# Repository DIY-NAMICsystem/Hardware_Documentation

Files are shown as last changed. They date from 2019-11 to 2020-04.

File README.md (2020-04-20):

# DIY-Nautiyal Arduino Modular Instrumental Conditioning (DIY-NAMIC) Boxes

<p align="center">
    <br>
    <i> Mouse retrieving water reward during behavioral testing in the DIY-NAMIC system </i>
</p>

<p align="left">
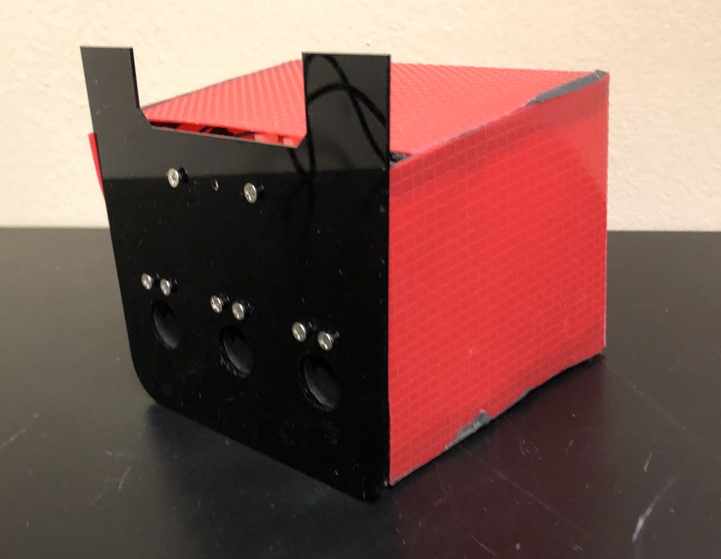
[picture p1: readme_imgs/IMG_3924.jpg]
  <br>
    <b><i> Assembled DIY-NAMIC hardware </b> </i>
    <br>
    <br>
</p>

<p align="left">
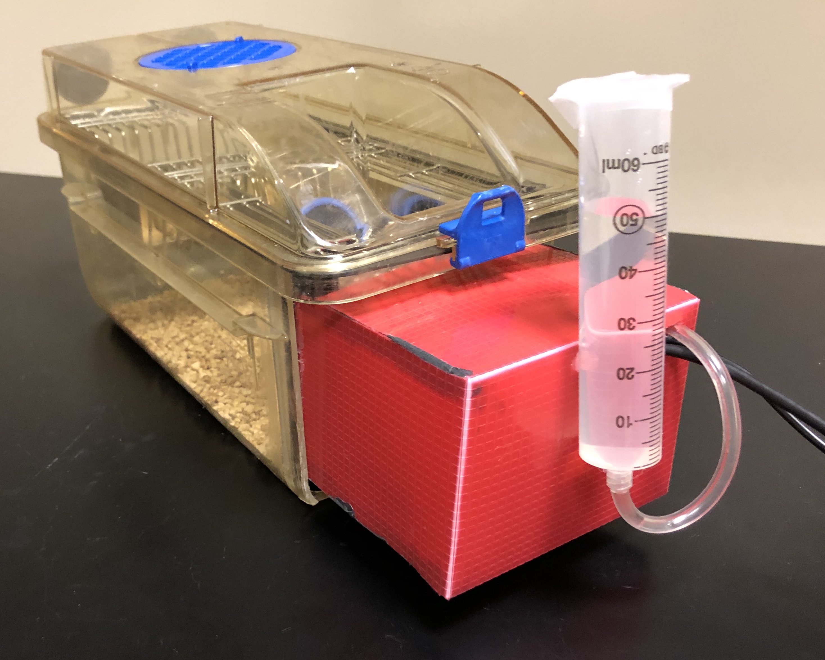
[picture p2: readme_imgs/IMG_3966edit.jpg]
  <br>
    <b><i> DIY-NAMIC cage </b></i>
</p>

<p align="left">
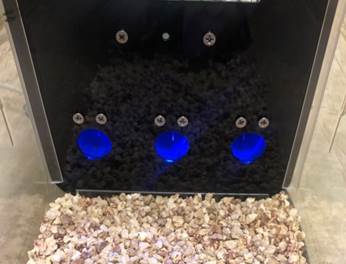
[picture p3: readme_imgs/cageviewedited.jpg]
  <br>
    <b><i> Mouse perspective </b> </i>
    <br>
    <br>
</p>

<p align="left">
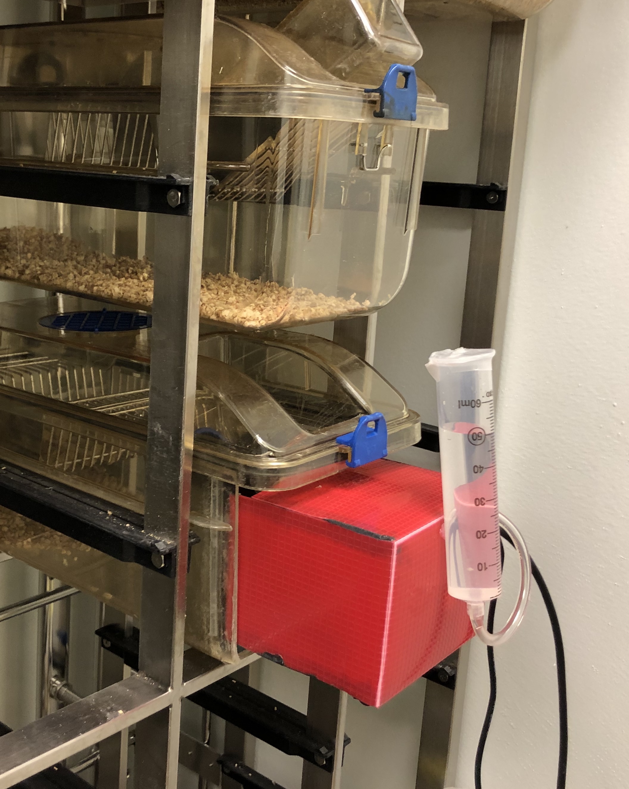
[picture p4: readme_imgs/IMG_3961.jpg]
  <br>
    <b><i> DIY-NAMIC testing is compatible with ventilated high-density racked cages </b> </i>
    <br>
    <br>
</p>

___

### What is DIY-NAMIC?

The DIY-NAMIC box is a customizable, low-cost apparatus for automated homecage operant behavioral testing. Made with Arduino microprocessor, 3D printed parts, and various *off-the-shelf* components, the boxes enable 24-hour data collection, significantly increasing trials/day without food or water restriction, and allowing for self-initiated trials during rodent's dark/active phase.  

Most importantly, this is an open-source project - any contributions / suggestions / feedback are welcome and appreciated!

___
### Benefits of DIY-NAMIC boxes.

1. Decreased Experiment Length <br>
Rodents have 24 hour access self-initiated trials allowing hundreds of trials per day. This allows for faster testing, reducing the number of days that many standard operant paradigms typically takes to run. This also permits testing during developmental time periods which can be very limited in rodents.

2. Inexpensive compared to commercially available operant testing chambers <br>
All the materials used to make one DIY-NAMIC box cost around $200, compared to$4000-$10,000 for the commercially-available units, which have limited customizability.

3. No food or water restriction <br>
Mice consume their normal daily intake of water, and no food deprivation is required.  The sated condition is important for the interpretation of many behavioral effects.  Additionally, this allows testing during development when food/water deprivation can be deleterious to growth.

4. Reduced daily experimenter effort <br>
There is minimal daily effort required from the experimenter, since mice are living in their homecage, and data is logged in realtime.

5. More ethologically-relevant testing <br>
Through self-initiated trials, mice can perform during their standard dark/active phase of the light-dark cycle. 

___
### Overview

The purpose of this repository is to provide **hardware manuals, documentation, and code** for anyone who would like to use and/or modify the DIY-NAMIC system.

#### Contents

* [**Chapter 0 - Background and Introduction**](https://github.com/DIY-NAMICsystem/Hardware_Documentation/tree/master/Chapter_0.Background_and_Introduction) 
* [**Chapter 1 - Getting Started - Essential Tips and Tricks**](https://github.com/DIY-NAMICsystem/Hardware_Documentation/tree/master/Chapter_1.Getting_Started-Essential_Tips_and_Tricks)
* [**Chapter 2 - Modifying the Rodent Cage**](https://github.com/DIY-NAMICsystem/Hardware_Documentation/tree/master/Chapter_2.Modifying_Rodent_Cage)
* [**Chapter 3 - OM1 Shield**](https://github.com/DIY-NAMICsystem/Hardware_Documentation/tree/master/Chapter_3.OM1_Shield)
* [**Chapter 4 - Component Assembly - LED**](https://github.com/DIY-NAMICsystem/Hardware_Documentation/tree/master/Chapter_4.Component_Assembly-LED)
* [**Chapter 5 - Component Assembly - Infrared Detectors**](https://github.com/DIY-NAMICsystem/Hardware_Documentation/tree/master/Chapter_5.Component_Assembly-Infrared_Detectors)
* [**Chapter 6 - Component Assembly - Solenoid Valves**](https://github.com/DIY-NAMICsystem/Hardware_Documentation/tree/master/Chapter_6.Component_Assembly-Solenoid_Valves)
* [**Chapter 7 - Component Assembly - Reward Spout**](https://github.com/DIY-NAMICsystem/Hardware_Documentation/tree/master/Chapter_7.Component_Assembly-Reward_Spout)
* [**Chapter 8 - Wiring and Soldering**](https://github.com/DIY-NAMICsystem/Hardware_Documentation/tree/master/Chapter_8.Wiring_and_Soldering)
* [**Chapter 9 - Final Assembly**](https://github.com/DIY-NAMICsystem/Hardware_Documentation/tree/master/Chapter_9.Final_Assembly)

* [**Appendix - Bill of Materials**](https://github.com/DIY-NAMICsystem/Hardware_Documentation/tree/master/Bill_of_Materials)

____
### Other open-source projects in the behavioral neuroscience community

1. [Feeding Experimentation Device (FED) - Kravitz Lab](https://github.com/KravitzLab/FED)
2. [CombiCage - Loos Lab](https://www.ncbi.nlm.nih.gov/pmc/articles/PMC5309744/)
3. [ArControl - Li Lab](https://github.com/chenxinfeng4/ArControl)
4. [Openmaze.org](http://openmaze.org/) - open source hardware and software for behavioral neuroscience
5. [Openbehavior.com](http://openbehavior.com/) - repository of open source tools for advancing behavioral neuroscience research]

### Development
_____

### Contributions and Thanks
_____

A big thanks to **Andrew R. Alvarenga** for his generous support and suggestions regarding hardware. Thank you for also allowing me to use the machine shop and test out different prototypes of the 3D printed parts on the 3D printer.

Thank you to undergraduate researchers **Bonnie Shea** and **Selin Capan** for assisting with daily running of the code.

#### Contact

For any questions or issues, contact **Jun Ho Lee** at jun.ho.lee@dartmouth.edu or **Katherine Nautiyal** at katherine.nautiyal@dartmouth.edu.

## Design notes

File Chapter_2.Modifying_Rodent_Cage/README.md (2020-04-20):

### Introduction

The DIY-NAMIC system utilizes a rodent homecage for behavioral testing. In this chapter, the standard rodent cage used in ventilated high-density racked systems is modified for use with the DIY-NAMIC system. Using a Dremel to cut a cross-section of the cage, U-channels are attached on the bottom and the sides of the cage, allowing a laser cut plexiglass wall to be slotted in.

### Rodent Cages

This section will require modification based on the available rodent caging systems.

The plexiglass wall must be modified to fit the relevant homecage. They can be modified from our design [(https://github.com/DIY-NAMICsystem/Hardware_Documentation/tree/master/Ponoko_Final)], and cut at Ponoko.com.

> This **location** was chosen due to the design of the cage hopper and the plexiglass. Positioning the U-channel at this location will minimize the gaps between the metal hopper and the plexiglass **(Figure 4 and Figure 5).**

For the purposes of exposing the cross-section, draw a line at the 5cm mark (see yellow arrow) at an angle **(Figure 2)** on both sides of the cage. These lines will always be posterior relative to the bottom U-channel position and thus will serve as good guidelines for cutting the cage later.

<p align="center">
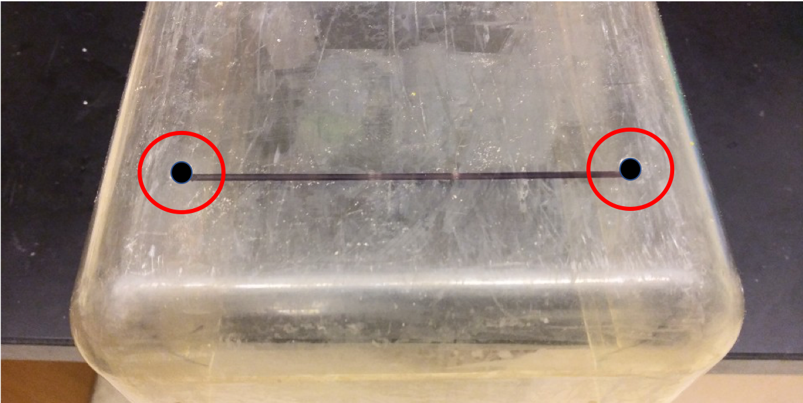
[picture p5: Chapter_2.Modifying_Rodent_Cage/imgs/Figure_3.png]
    <br><br>
    <b><i>Figure 3:</b> The two protruding circles (filled with black circles within red bounded circles) are connected with a black Sharpie marker. This will later serve as the bottom U-channel position. </i>
</p>

<p align="center">
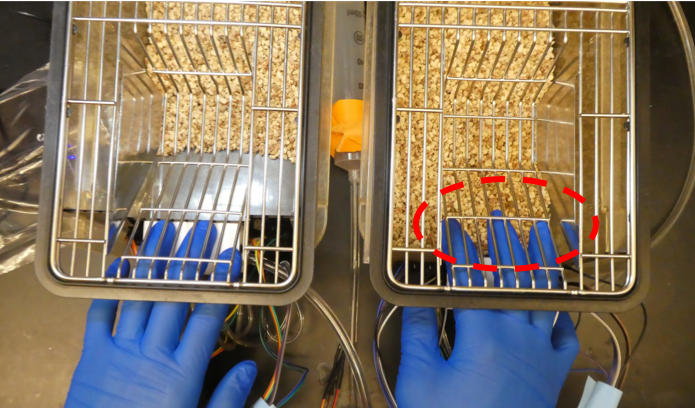
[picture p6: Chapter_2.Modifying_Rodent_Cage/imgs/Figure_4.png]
    <br><br>
    <b><i>Figure 4:</b> Faulty positioning of the U-channel will result in gaps between the plexiglass and the metal hopper (Red Circle) </i>
</p>

<p align="center">
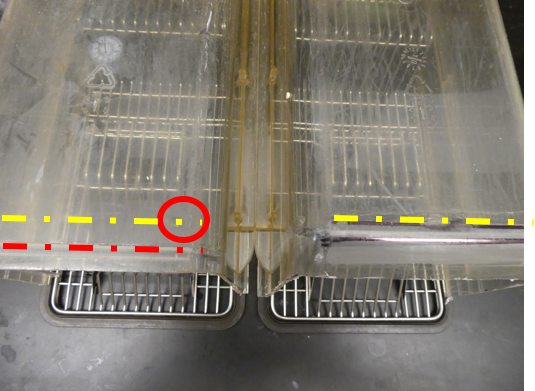
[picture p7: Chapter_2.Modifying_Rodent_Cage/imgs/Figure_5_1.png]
    <br><br>
    <b><i>Figure 5:</b> Yellow dotted lines indicate the correct location for positioning the bottom U-channel. Red dotted lines indicate a faulty position that will create a gap between the metal hopper and the plexiglass. </i>
</p>

### Cutting the Cage

When cutting the cage, make sure to cut the sides first. Remember that the sharpie mark at the bottom is where the U-channels are going to align, **NOT** where it will be cut. Cutting the sides first will prevent you from making that mistake.

<p align="center">
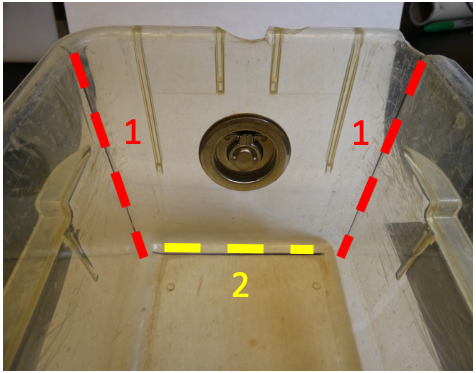
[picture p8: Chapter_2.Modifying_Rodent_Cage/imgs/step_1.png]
step1
    <br><br>
    <b><i>Step 1:</b> Cut the cage according to the numbers shown - Sides (Red) first and then the bottom (Yellow) of the cage. </i>
</p>

<p align="center">
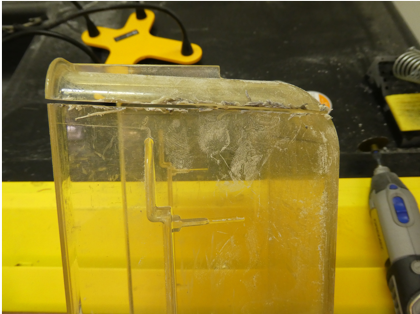
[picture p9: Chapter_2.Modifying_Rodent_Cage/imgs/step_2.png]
step2
    <br><br>
    <b><i>Step 2:</b> Cutting along the sharpie mark along the two sides </i>
</p>

<p align="center">
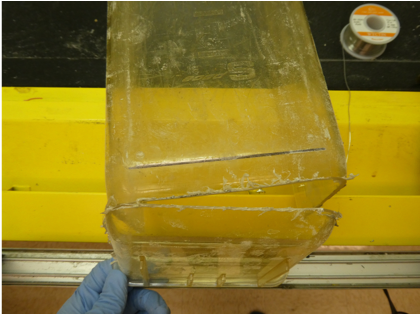
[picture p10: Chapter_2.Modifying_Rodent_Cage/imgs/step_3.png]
step3
    <br><br>
    <b><i>Step 3:</b> All three sides (two sides + one bottom) have been cut and ready to be separated from the main cage body. </i>
</p>

The Dremel rotary tool will produce a lot of fine dust so work in a well-ventilated area. After the initial cut, wash off the fine dust by running the cage under water. After thoroughly drying it, you may also want to use the belt grinder to sand down the sides for a smoother, cleaner finish.

<p align="center">
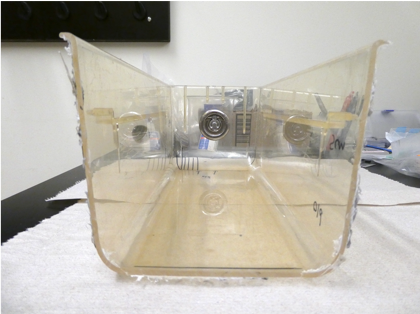
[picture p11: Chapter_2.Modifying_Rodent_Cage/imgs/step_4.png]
step4
    <br><br>
    <b><i>Step 4:</b> Cross Section of the cage right after the Dremel cut. Notice the rugged, sharp edges. </i>
</p>

<p align="center">
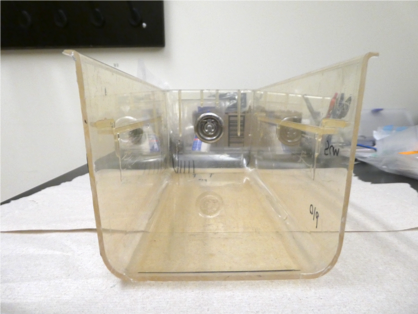
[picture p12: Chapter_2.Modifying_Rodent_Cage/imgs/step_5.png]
step5
    <br><br>
    <b><i>Step 5:</b> Cross section of the cage after sanding it down with the belt grinder. </i>
</p>

### Attaching the U-Channels

<p align="center">
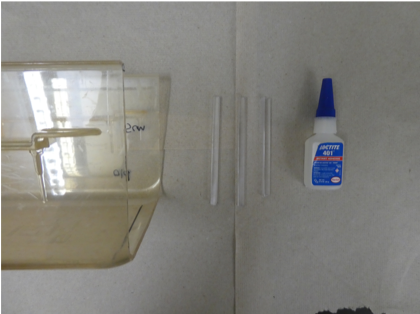
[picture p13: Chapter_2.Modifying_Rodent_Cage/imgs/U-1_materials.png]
materials
    <br><br>
    <b><i>Materials Needed:</b> Loctite Glue (401) / U-channels / Rodent Cage </i>
</p>

<p align="center">
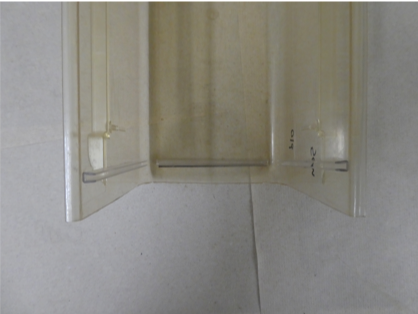
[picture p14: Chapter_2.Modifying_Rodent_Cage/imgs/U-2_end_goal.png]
endgoal
    <br><br>
    <b><i>End Goal:</b> Picture of the completed modified cage after attaching the U-channels </i>
</p>

Two U-channels (11.3cm long) will go on the sides and one U-channel (10.3cm long) will go on the bottom.

The U-channels serve as guides for the plexiglassto be slid in. Therefore, all three should be aligned and flat with the surface of the cage. It is easier to align all three of them together if the bottom is attached first. Then, align the side U-channels by using the bottom U-channel as a reference point.

<p align="center">
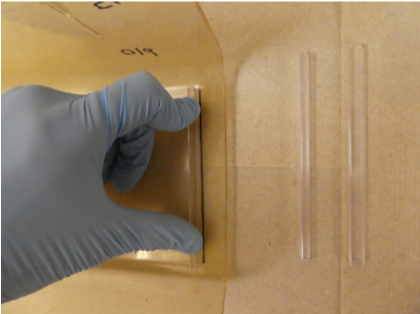
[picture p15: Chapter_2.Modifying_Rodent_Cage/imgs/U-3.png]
u1
    <br><br>
    <b><i>Step 1:</b> Attaching the bottom U-channel first. Apply Loctite glue along the back of the U-channel and align it along the black sharpie mark and hold it down for a few seconds to get a good attachment. Let it cure overnight. </i>
</p>

<p align="center">
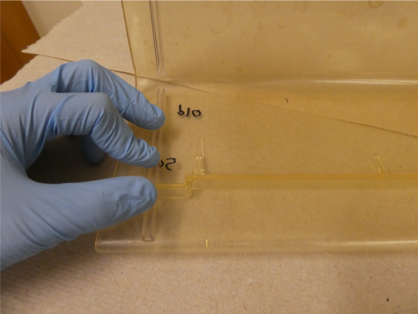
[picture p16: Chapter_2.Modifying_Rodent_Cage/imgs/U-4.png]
u2
    <br><br>
    <b><i>Step 2:</b> Attaching the side U-channels. Align them using the bottom U-channel as a reference point. Use the same steps as in <b> Step 1. </b> </i>
</p>

#### Using Loctite Glue, which allows for normal cage washing and high heat sanitization. 

> After cleaning surfaces with ethanol, apply Loctite glue generously and attach the U-channels to the rodent cage. 401 Loctite is very watery so you will have some time to wiggle the U-channel around if you didn’t get the placement correct the first time. To make sure there is a good adhesion, let the Loctite cure for a few hours, overnight if you have time.

Once the Loctite glue has cured and the U-channels are securely fastened, test out the alignment by sliding in your Plexiglass along the U-channel railings like in **Step 3**. Make sure to try the cage top as well to check for gaps!

<p align="center">
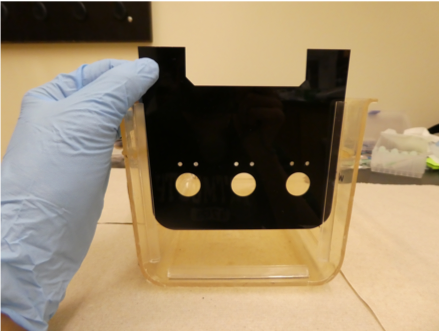
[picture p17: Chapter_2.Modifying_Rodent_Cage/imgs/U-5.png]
u3
    <br><br>
    <b><i>Step 3:</b> Sliding the plexiglass along the U-channel railings for testing purposes </i>
</p>

###### END OF CHAPTER

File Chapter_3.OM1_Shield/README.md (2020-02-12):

# Chapter 3. OM1 Shield

Arduino shields allow functionalities to be added to the basic microprocessor.  DIY-NAMIC boxes require this because of the additional voltage needed for the solenoid components (above what the ATMEGA328P microprocessor can handle).  The build protocol described here starts with a printed circuit board onto which necessary components are soldered on.  The OpenMaze.org OM1 shield was designed by [openmaze.org](http://openmaze.org/)), and purchased from OSH Park https://oshpark.com/shared_projects/ea7NpG7p.

### OM1 Printed circuit board 

1)	7 pins broken out to Power-Ground-Input-Output (PGIO) ports (red box)  
> **IMPORTANT:** Breakout pins 7,8,9,10 are not connected to normal Arduino power. In order to supply 5V power to these 4 breakout pins, you must connect the pink circle (arrow) with the other pink circle with a jumper wire. For 12V power, connect the pink circle (arrow) with the green circle (refer to PCB connection diagram for explanation).  
2)	socket for the H-bridge chip (green box)  
3)	4 pins broken out for solenoid valves (blue box)  
4)	a connector for MPR121 capacitive touch sensor (yellow box) - not used in this version of DIY-NAMIC boxes  

<p align="center">
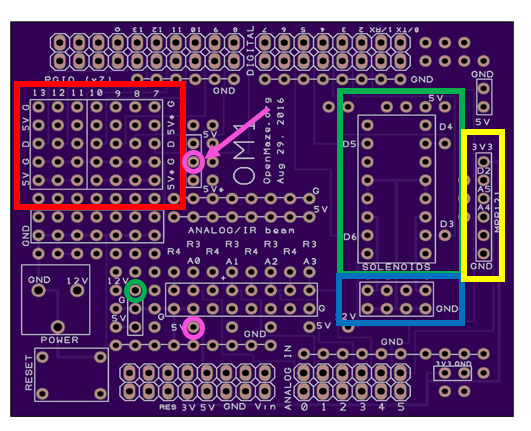
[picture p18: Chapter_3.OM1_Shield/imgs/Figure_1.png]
     <br><br>
    <b><i>Figure 1:</b> Diagram of the OM1 Shield. Source: <a href="http://www.openmaze.org/ "> Link </a> </i>

</p>

Note that the picture above is the bare printed circuit board (PCB) on to which the necessary components must be attacehd! This section will detail the steps to solder on the necessary components.

<p align="center">
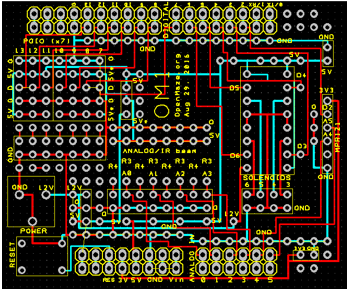
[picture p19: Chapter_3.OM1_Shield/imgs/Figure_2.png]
    <br><br>
    <b><i>Figure 2:</b> Small version of all the electrical connections within the OM1 Shield. Red and blue lines are used just to differentiate connections. They do not carry any meaning.
</p>

### Components

Below is a picture of the components which are soldered on to the OM1 shield.

<p align="center">
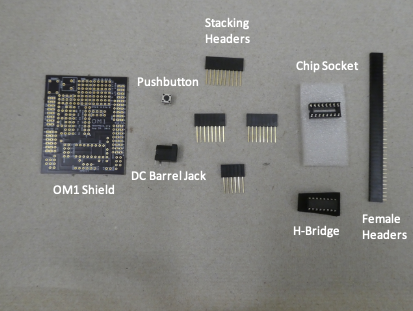
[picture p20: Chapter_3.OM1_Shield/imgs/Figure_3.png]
    <br><br>
    <b><i>Figure 3:</b> List of components needed to make a functioning OM1 Shield.</i>
</p>

Components for building shield:
For more details and where to purchase them, refer to the [Bill of Materials](https://github.com/jhl0204/AIM-Hardware-Documentations/wiki/Bill-of-Materials)

- OM1 Shield Printed Circuit Board
- pushbutton
- 2.1mm DC Barrel Jack
- Stacking Headers (1x10 (1) / 1x8 (2) / 1x6 (1))
- Chip Socket + H Bridge**
- Female + Male Headers

##### **What is a H-Bridge? 

> H-bridges are electric circuits that “amplify” low power signals. Since Arduinos have a 5V limit, H-bridges are used to power solenoids which require 9V input. H-bridges are also commonly used to drive motors using Arduinos. The H-bridge we are using is a dual H-Bridge motor driver (L293D) that can run four solenoids at once with a limit of 600mA per channel. The OM1 shield allows for 1 H-bridge.
Links for more information:   
1) [Making H-Bridge on a Breadboard](https://www.instructables.com/id/H-Bridge-on-a-Breadboard/)  
2) [Basics of H-Bridge](http://www.modularcircuits.com/blog/articles/h-bridge-secrets/h-bridges-the-basics/)  
3) [Driving a DC Motor using H-Bridge](http://hades.mech.northwestern.edu/index.php/Driving_a_high_current_DC_Motor_using_an_H-bridge)  

### Soldering Diagram

Components are soldered to the OM1 shield according to the diagram below. For best solder results however, refer to tips in [Essential Tips and Tricks](https://nbviewer.ipython.org/github/jhl0204/DNAMIC-Hardware-Documentations/blob/master/Chapter_1.Getting_Started-Essential_Tips_and_Tricks/1_Essential_Tips_and%20Tricks_vF.ipynb) before starting.

<p align="center">
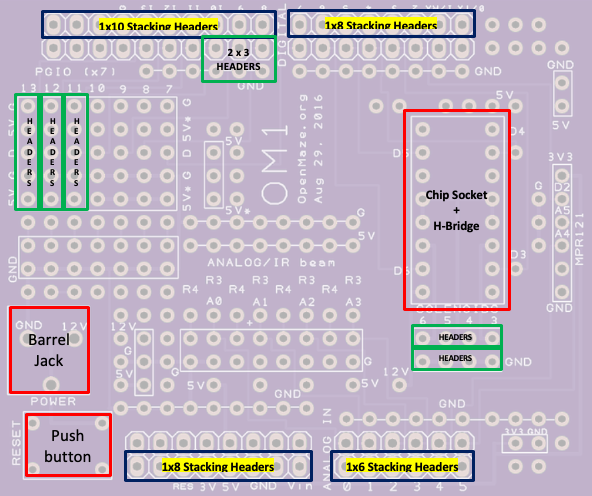
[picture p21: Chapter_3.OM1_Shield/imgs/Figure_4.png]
    <br><br>
    <b><i>Figure 4:</b> The physical components are color coded with red, stacking headers with dark blue, and female headers with green. When soldering on any components, make sure to adjust the pins if necessary so that they would fit into the holes on the board.</i>
</p>

### Note on the Chip Socket

The chip socket and the H-bridge chip have directionality. When soldering on the chip socket and inserting the H-bridge chip, make sure the semicircle is aligned according to the arrow. The semicircle in the chip determines the location of pin 1. As can be seen from **Figure 6**, pin 1 starts from the upper left corner where the semicircle is located. For more details on how the H-bridge connects to the solenoid, see the diagram below While the socket doesn’t actually have directionality (only H-Bridges do), it is recommened to align the socket to ensured proper H-bridge directionality.

<p align="center">
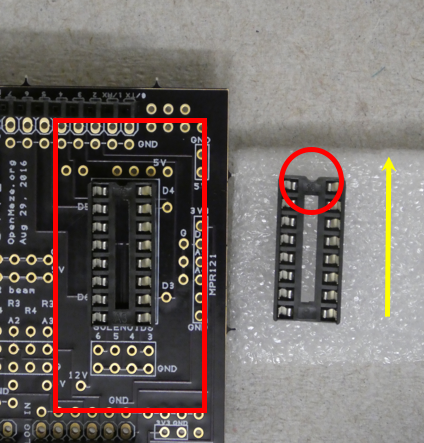
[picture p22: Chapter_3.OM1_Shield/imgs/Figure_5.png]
    <br><br>
    <b><i>Figure 5:</b> Note how the half circle in the chip socket is aligned in the direction of the yellow arrow. Red box is explained in detail in <b> Figure 6. </b></i>
</p>

<p align="center">
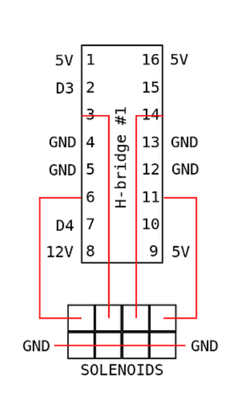
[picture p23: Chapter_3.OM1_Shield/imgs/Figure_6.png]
    <br><br>
    <b><i>Figure 6:</b> Diagram of H-bridge used in OM1 Shield. <a href="http://www.openmaze.org/"> Source </a> </i>
</p>

### Attaching the shield to the Ardunino UNO
Once the components are soldered to the OM1 PCB shield, the shield is attached to the Arduino via the stacking headers

<p align="center">
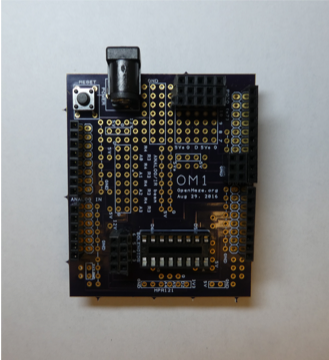
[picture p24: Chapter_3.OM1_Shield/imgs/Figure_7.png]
    <br><br>
    <b><i>Figure 7:</b> Top view of the finished OM1 Shield </i>
</p>

<p align="center">
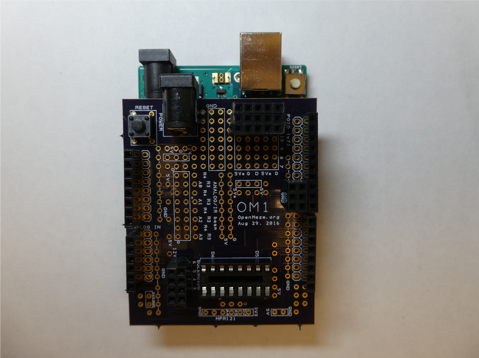
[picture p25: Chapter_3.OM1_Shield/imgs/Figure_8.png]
    <br><br>
    <b><i>Figure 8:</b> OM1 Shield stacked on top of the Arduino. </i>
</p>

<p align="center">
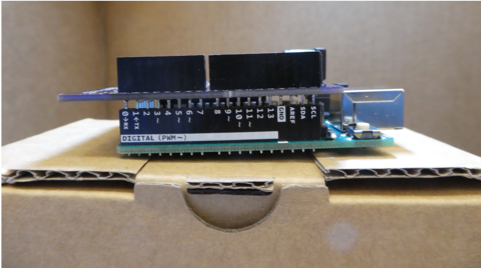
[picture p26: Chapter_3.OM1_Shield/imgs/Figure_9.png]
    <br><br>
    <b><i>Figure 9:</b> Side view of the Arduino + OM1 Shield </i>
</p>

<p align="center">
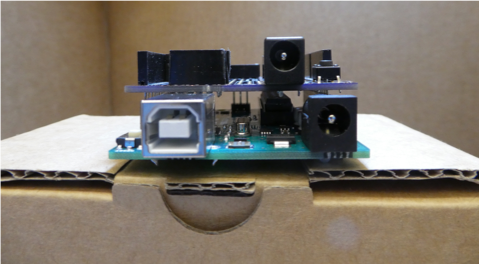
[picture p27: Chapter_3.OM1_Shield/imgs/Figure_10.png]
    <br><br>
    <b><i>Figure 10:</b> Front view of the Arduino + OM1 Shield </i>
</p>

###### END OF CHAPTER

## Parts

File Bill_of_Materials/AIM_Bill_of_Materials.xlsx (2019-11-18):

Parts per Box
Materials | Vendor | Serial # | Notes | Cost | # per cage | Notes on alternative sources for parts | URL | Total Cost
Arduino | Arduino Store | - | Arduino Uno Rev 3 | $22 / ea | 1 | Other Arduinos will work, but may require changes to OM1 Shield, code and wiring | https://store.arduino.cc/usa/arduino-uno-rev3 | $22.00
OM1 Shield | oshpark | N/A (customized) | Design from openmaze.org | $28.05 / 3 items | 1 | Other shields have not been tested - Usage of this shield is recommended | https://oshpark.com/shared_projects/ea7NpG7p | $9.00
Nose ports | Shapeways | N/A (customized) | / | $14.1 / ea | 3 | Customizable depending on use-case and hardware available | https://www.shapeways.com/ | $42.30
Manifold Encasing | Shapeways | N/A (customized) | / | $20 / ea | 1 | Customizable depending on use-case and hardware available | https://www.shapeways.com/ | $20.00
Plexiglass | Ponoko | N/A (customized) | Acrylic Black / 1.5mm thickness | $6.3 / ea | 1 | Customizable depending on use-case and hardware available | https://www.ponoko.com/ | $6.30
Barrel Jack | Adafruit | #373 | 2.1mm DC Barrel Jack | $0.86 / ea | 1 | Any barrel jack of the same specifications will work | https://www.adafruit.com/product/373 | $0.86
Pushbuttons | Amazon | - | 100 items per package | ~$6 / pkg | 1 | Any pushbutton with same internal wiring will work | https://www.amazon.com/CO-RODE-Tact-Button-Switch-6x6x5mm/dp/B00W0YUV1W | $6.00
H-bridge | Adafruit | #807 | Dual H-Bridge for DC or Steppers – 600mA | $2.66 / ea | 1 | Other H-Bridges have not been tested - Usage of this H-Bridge is recommended | https://www.adafruit.com/product/807 | $2.66
IC socket | Adafruit | #2203 | For 16-pin 0.3” Chips | $0.86 / ea | 1 | Other IC sockets must be compatible with the number of pins of the H-Bridge and OM1 Shield | https://www.adafruit.com/product/2203 | $0.86
Arduino Wall Power Supply | Amazon | - | AC 100-240V to DC 9V 1A | $8 / ea | 1 | Other Arduino power supply with same or better specifications will work | https://www.amazon.com/ELEGOO-100V-240V-Converter-Adapter-Certificate/dp/B074BRR5YN | $8.00
Rodent Cage | N/A (Lab) | N/A (lab supplied) | / | N/A | 1 | Use of alternative rodent cage will require design changes to 3D printed noseports and plexiglass | N/A | $0.00
U-Channels | McMaster Carr | 1753K61 | 4ft long | $3.88 / ea | 1 | Dimension of U-channel must be compatible with the thickness of plexiglass | https://www.mcmaster.com/catalog/125/3729 | $3.88
Screws | McMaster Carr | 91771A107 | Philips Flat Head: 4-40 Thread Size, 5/16" Long | $4.53 / pkg | - | Other screws must be compatible with the screw hole dimensions in 3D printed noseports | https://www.mcmaster.com/catalog/125/3141 | $4.53
Photo interrupter | Pimoroni | GP1A57HRJ00F | - | $2.5 / ea | 3 | Usage of other photointerrupters might require change to 3D noseport design - Usage recommended | https://shop.pimoroni.com/products/photo-interrupter-gp1a57hrj00f | $7.50
Solenoids | The Lee Company | LHDA0533115H | 3 port ported | Quoted Price | 3 | Other solenoids have not been tested and may require changes to tubing assembly - Usage recommended | https://www.theleeco.com/products/electro-fluidic-systems/solenoid-valves/control-valves/lhd-series/3-port/ported/ | $30.00
LEDs | Amazon | - | blue light - 100 items per package | ~$8 / pkg | 3 | Any LED of same specifications will work | https://www.amazon.com/dp/B07MM8T1XX/ref=twister_B07QB2FYFD?_encoding=UTF8&psc=1 | $8.00
3-way manifolds | McMaster Carr | 5203K929 | Push to connect 3 outlet manifold, 1/8” OD | $12.66 / ea | 1 | Any manifold with same tubing dimensions will work | https://www.mcmaster.com/catalog/125/237 | $12.66
Luer Lock adapter | Cole Parmer | # EW-45518-00 | Male Luer with lock ring x 1/16" hose barb, 25/pk | $13.30 / pkg of 25 | 3 adapters | Any adapter with same dimensions will work | https://www.coleparmer.com/i/cole-parmer-male-luer-with-lock-ring-x-1-16-hose-barb-pp-25-pk/4551800 | $13.30
Tubing (1/16” ID) | Component Supply | TET-062A | Tygon E-3603 1/16” ID x 1/8” OD x 1/32” Wall | $0.32 / ft | 3 feet | Any tubing with the same dimensions will work | http://www.componentsupplycompany.com/product-pages/tygon-e-3603-lab-tubing.php | $0.96
Tubing (1/8” ID) | Component Supply | TET-125B | Tygon E-3603 1/8” ID x 1/4” OD x 1/16” Wall | $1.07 / ft | 3 feet | Any tubing with the same dimensions will work | http://www.componentsupplycompany.com/product-pages/tygon-e-3603-lab-tubing.php | $1.32
21G Needles | Thermo Fisher | N/A (lab supplied) | Precision Glide Needles (0.8mm x 50mm) (21G) | N/A | 3 | Any needle with same specifications will work | N/A | $0.00
60cc Syringes | Thermo Fisher | N/A (lab supplied) | - | N/A | 1 | Any 60cc Luer Lock compatible syringe will work | N/A | $0.00
 |  |  |  |  |  |  | Total Cost (per box): | $200.13
Initial Upfront Cost
Materials | Vendor | Serial # | Notes | Cost | # per cage | Notes on alternative sources for parts | URL | Total Cost
Multimeter | Amazon | - | w/ Continuity testing option | $10.99 / ea | N/A | Any multimeter will work | https://www.amazon.com/AstroAI-Digital-Multimeter-Voltage-Tester/dp/B01ISAMUA6 | $10.99
Resistor Set (1K / 10K) | Amazon | - | 1/4 W Metal Film Resistors | $11.00 / set |  | Any 1/2W or 1/4W resistor will work | https://www.amazon.com/Elegoo-Values-Resistor-Assortment-Compliant/dp/B072BL2VX1 | $11.00
30cm F-M Jumper Wires | Amazon | - | 120 pcs per pkg | $8.99 / pkg |  | Any jumper wire will work. Change in length might require different setup of the box | https://www.amazon.com/EDGELEC-Breadboard-Optional-Assorted-Multicolored/dp/B07GD2PGY4?s=industrial | $8.99
Shrink Tubes | Amazon | - | 2.0mm ~ 3.0mm in size | $7.49 / pkg |  | Any shrink tubes with same dimensions will work | https://www.amazon.com/532pcs-Shrink-Tubing-innhom-Approved/dp/B075WR9FVL?s=industrial | $7.49
Stacking Pin Set | Amazon | - | - | $13.99 / set |  | Any Arduino compatible stacking pins will work | https://www.amazon.com/Hilitchi-110pcs-Arduino-Stackable-Assortment/dp/B01IP60YQA | $13.99
Headers (Female + Male) | Amazon | - | 2.54mm spacings (standard) | $7.49 / pkg |  | Any Arduino compatible headers will work | https://www.amazon.com/DEPEPE-2-54mm-Headers-Arduino-Prototype/dp/B074HVBTZ4 | $7.49
Soldering Iron | Amazon | - | Weller WES51 Analog Soldering Station | $148 |  | Any soldering iron will work but usage of this iron is recommended (pretty high quality) | https://www.amazon.com/Weller-WES51-Analog-Soldering-Station/dp/B000BRC2XU?s=gateway | $148.00
Dremel Rotary Tool | Amazon | - | Dremel 4300-5/40 Rotary Tool Kit | $96 |  | Any rotary tool will work | https://www.amazon.com/Dremel-4300-5-Performance-Attachments-Accessories/dp/B01M1SJNVU?s=gateway | $96.00
EZ Lock Cutting Kit for Dremel | Amazon | - | Kit for Metal and Plastic | $28 |  | Any EZ Lock Component will work as long as there is one for metal and one for plastic | https://www.amazon.com/Dremel-EZ688-01-Cutting-Metal-Plastic/dp/B002Q8T4OM | $28.00
Multi Purpose Lighter | Amazon | - | For use with heat shrink tubes | $9 |  | Any lighter will work | https://www.amazon.com/BIC-Multi-Purpose-Classic-Lighter-2-Pack/dp/B0742K1VMV | $9.00
 |  |  |  |  |  |  | Initial Investment Cost | $340.95

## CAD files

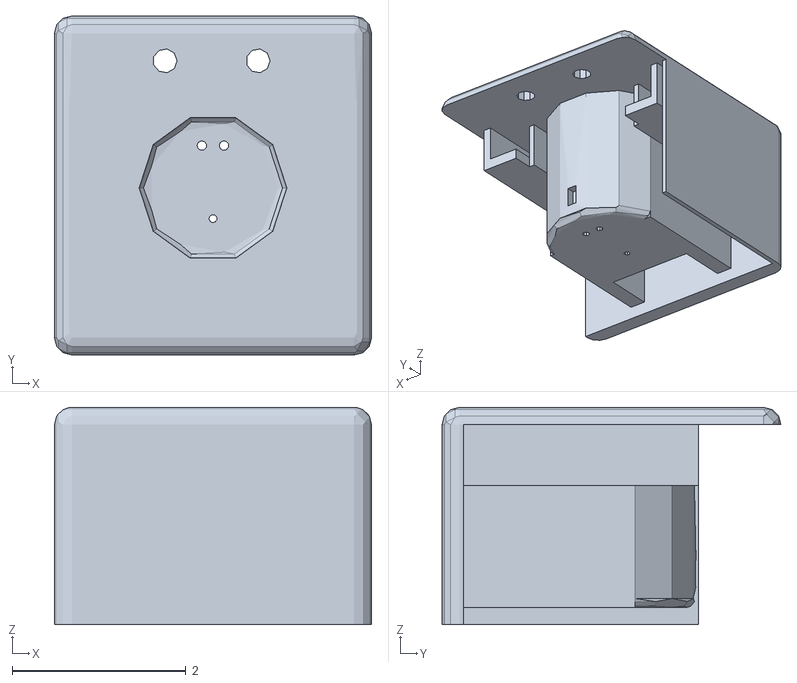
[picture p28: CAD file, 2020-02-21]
Shapeways_Final/Individual_Ports.stl
3.65 x 3.90 x 2.50

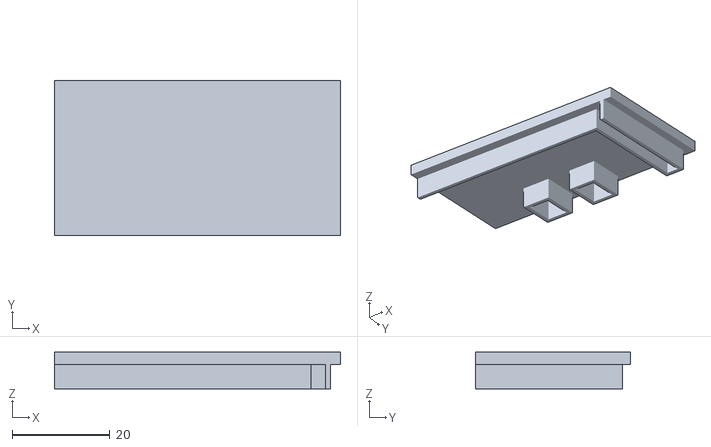
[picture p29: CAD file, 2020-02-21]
Shapeways_Final/manifold_encasing_top.stl
58.7 x 31.8 x 7.50

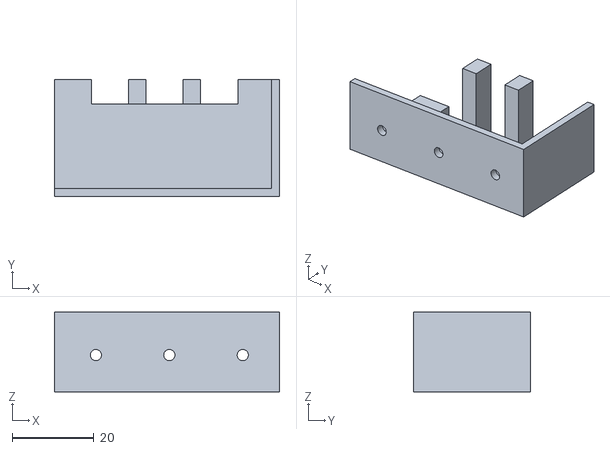
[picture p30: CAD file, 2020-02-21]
Shapeways_Final/manifold_encasing_bottom.stl
55.1 x 28.6 x 19.5

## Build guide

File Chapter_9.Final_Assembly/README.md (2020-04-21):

# Final Assembly

#### What you will learn:

How to build and assemble the box with the finished components.
___

### Introduction

With the modified cage, OM1 shield, and soldered components to the wires, they can now be assembled. 

### Materials

<p align="center">
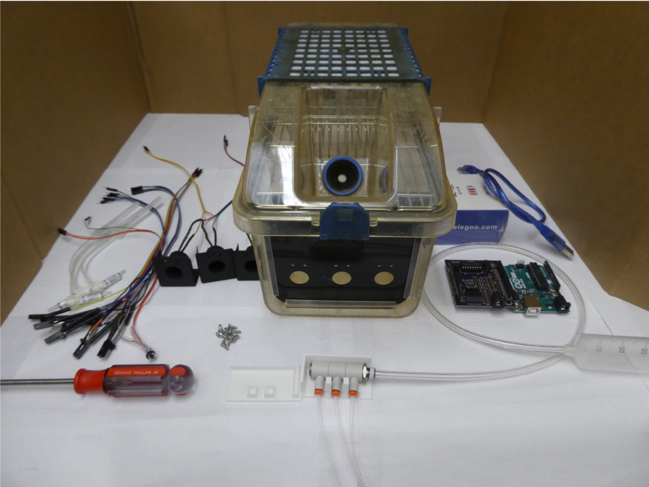
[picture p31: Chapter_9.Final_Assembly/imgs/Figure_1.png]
    <br><br>
    <b><i>Figure 1</b></i>
</p>

#### Components:

Components | Arduino | Others
------|:-------:| -----
LEDs (attached to noseport) | Arduino | Cage + Plexiglass
IR photo interrupters | OM1 Shield| Manifold + Syringe  
Solenoids + Tubing | Type A/B USB Cable | Screwdriver
 | Power Adapter | Screws (Phillips 4-40 x 5/16")

 ### 1) Assemble customized nose ports to Plexiglass

 <p align="center">
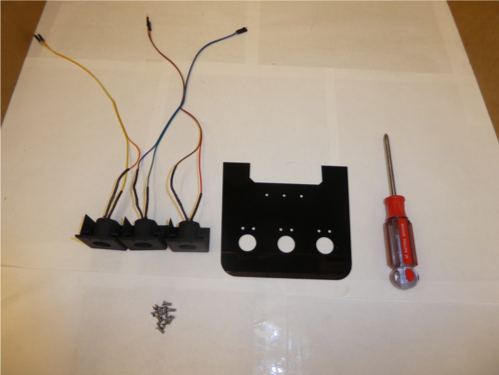
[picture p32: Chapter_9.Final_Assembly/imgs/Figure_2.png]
     <br><br>
     <b><i>Figure 2:</b> Materials Needed for noseport - plexiglass assembly</i>
 </p>

 Once the nose ports have the components attached, they can be screwed to the plexiglass. The ront-plate should look something like this:

 <p align="center">
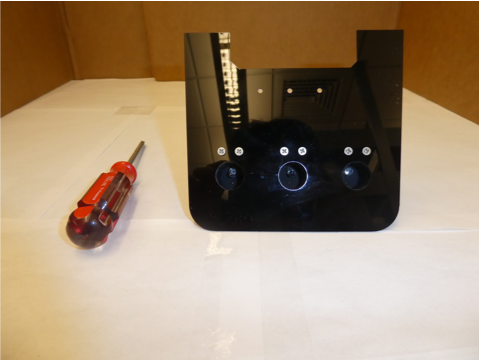
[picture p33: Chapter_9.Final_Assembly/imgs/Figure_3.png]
     <br><br>
     <b><i>Figure 3:</b> Front view of plexiglass (mice will face this side) </i>
 </p>

 <p align="center">
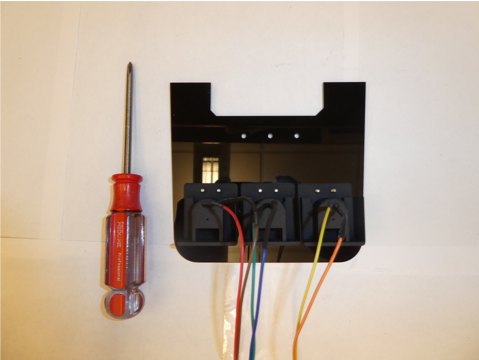
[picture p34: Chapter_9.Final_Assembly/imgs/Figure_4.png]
     <br><br>
     <b><i>Figure 4:</b> Back view of plexiglass (we will face this side) </i>
 </p>

 Remember that the rodents will be facing the flush side of the plexiglass. The wires will be on the back side, since we don’t want mice interacting and possibly chewing up all the wires.

 ### 2) Slide in the IRs into the nose port

 <p align="center">
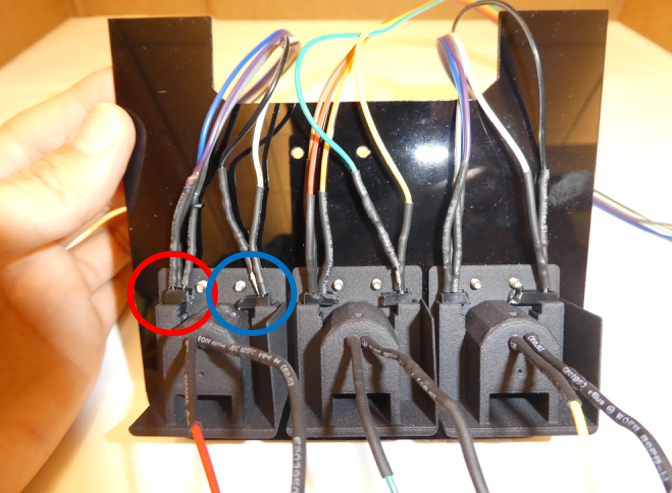
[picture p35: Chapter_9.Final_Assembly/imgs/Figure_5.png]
     <br><br>
     <b><i>Figure 5:</b> Make sure that the IR LEDs go into the right (blue circle) and the phototransistor goes into the left (red circle) </i>
 </p>

 Both parts of the IR (LED and phototransistor) will fit snugly into the nose port. However, make sure that the IR LED goes into the right (blue circle – 2 wires) and that the phototransistor goes into the left (red circle – 3 wires). This will help with wiring later when we connect them to the shield.

 ### 3)	Assemble the solenoids with the manifold and the syringe

 <p align="center">
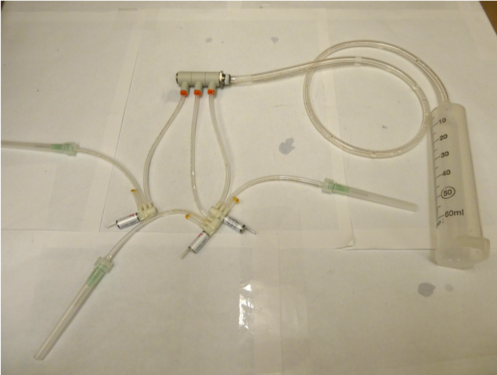
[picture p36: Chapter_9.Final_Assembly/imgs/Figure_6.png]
     <br><br>
     <b><i>Figure 6:</b> Picture of solenoids, manifold, and syringe after final assembly </i>
 </p>

 The solenoid valves assembled with the tubing are attached to the manifold, and the manifold is attached to the syringe with the larger tubing. See [Bill of Materials](https://github.com/jhl0204/AIM-Hardware-Documentations/wiki/Bill-of-Materials))

Also note that the solenoids valves don’t have the wires soldered on. Original female – male wires can be used for the solenoids since the solenoid valve leads are thick and the female encasings stay on. 

### 4) Screw in the manifold encasing

<p align="center">
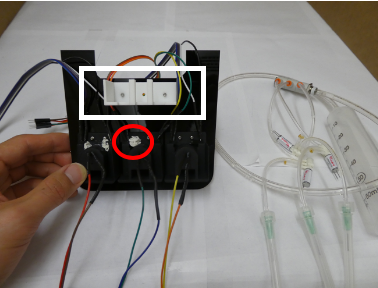
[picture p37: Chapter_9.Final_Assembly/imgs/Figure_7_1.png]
    <br><br>
    <b><i>Figure 7:</b> Screwing in the manifold encasing (white rectangular box) </i>
</p>

<p align="center">
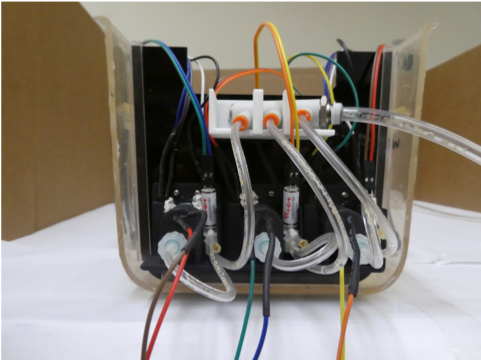
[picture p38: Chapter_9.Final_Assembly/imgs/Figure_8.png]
    <br><br>
    <b><i>Figure 8: </b> After set-up. Notice the manifold on top of the manifold encasing </i>
</p>

Screw in the manifold encasing into the plexiglass. 

<p align="center">
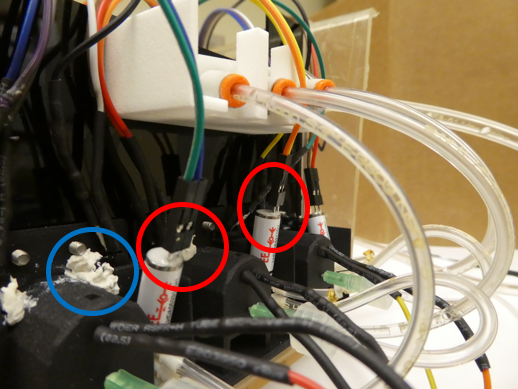
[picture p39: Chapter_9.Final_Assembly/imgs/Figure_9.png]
    <br><br>
    <b><i>Figure 9: </b> Note that the solenoid valves are fitted with normal female wires (red circle). </i>
</p>

### 5) Wiring to the OM1 Shield

Once all the components are attached to the plexiglass, they can be wired to the shield. For the LEDs and IRs, the GND should be connected to the GND rails on the shield. For the solenoids, the polarity does not matter. **Figure 10** shows where the components should go on the shield. The wiring is as follows: **pins 4, 5, 6 for solenoids** / **pins 8, 9, 10 for LEDs** and **pins 11, 12, 13 for IRs.**

<p align="center">
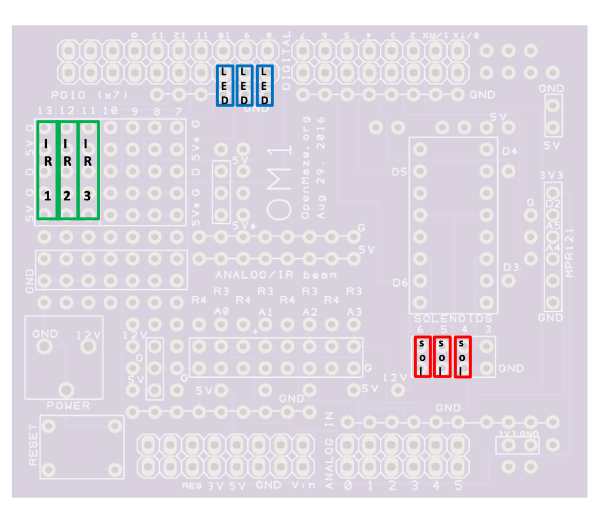
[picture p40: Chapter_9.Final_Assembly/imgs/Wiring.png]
    <br><br>
    <b><i>Figure 10: </b> Schematic showing where the components go on the shield </i>
</p>

### 6) Components completed
<p align="center">
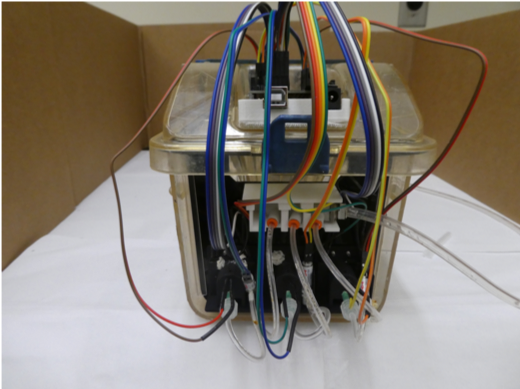
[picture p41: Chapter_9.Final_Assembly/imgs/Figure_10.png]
    <br><br>
    <b><i>Figure 11: </b> Front View of the completed DNAMIC box </i>
</p>

<p align="center">
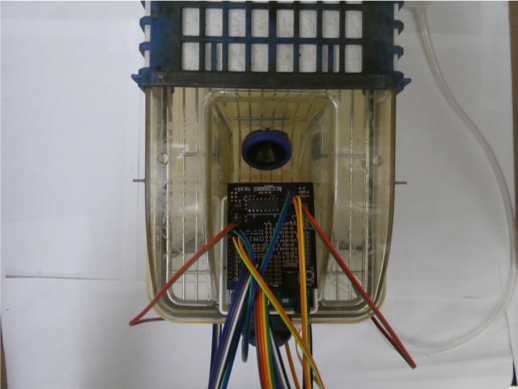
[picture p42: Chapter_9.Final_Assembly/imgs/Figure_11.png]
    <br><br>
    <b><i>Figure 12: </b> Top View of the completed DNAMIC box </i>
</p>

<p align="center">
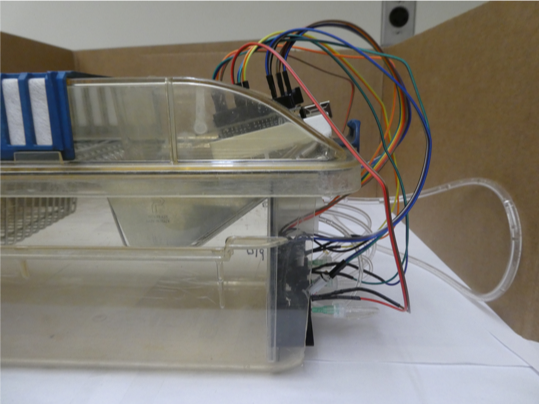
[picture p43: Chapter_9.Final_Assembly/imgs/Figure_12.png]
    <br><br>
    <b><i>Figure 13: </b> Side View of the completed DNAMIC box </i>
</p>

###### END OF CHAPTER

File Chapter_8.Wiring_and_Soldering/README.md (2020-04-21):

# Chapter 8. Wiring and Soldering

#### What you will learn:

How to wire the components (IR / solenoids / LEDs) to the jumper wires
____

### Introduction

Protoyping with a breadboard and jumper wires is a helfpul initial step. As things become more complicated and you know that your prototype works, you will want to make your project permanent by soldering / crimping components together.  

<p align="center">
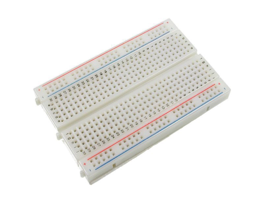
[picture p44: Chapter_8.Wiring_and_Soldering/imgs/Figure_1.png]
    <br><br>
    <b><i>Figure 1:</b> Simple Half-Breadboard </i>
</p>

<p align="center">
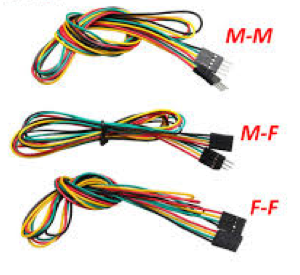
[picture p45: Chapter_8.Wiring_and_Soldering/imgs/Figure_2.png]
    <br><br>
    <b><i>Figure 2:</b> Three types of jumper wires: Male/Male, Male/Female, Female/Female </i>
</p>

### Hacking the Dupont connectors

When connecting components to the breadboard or generally connecting two points together, we slide in the male wire to the female jumper wire. We can do this thanks to the Dupont connectors at the end. Dupont connectors are standardized pins that are 0.1” (2.54mm) in width (same as Arduinos and breadboards).  

<p align="center">
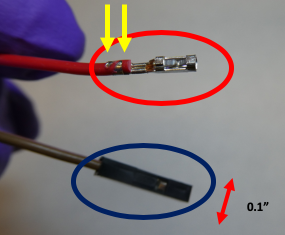
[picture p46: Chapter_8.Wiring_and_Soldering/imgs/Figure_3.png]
    <br><br>
    <b><i>Figure 3:</b> Female Dupont connectors (red) and Dupont connectors with housing (blue) </i>
</p>

<p align="center">
    <br><br>
    <b><i>Figure 4:</b> Male Dupont connector can fit into Female Dupont connector. </i>
</p>

You can see an example of a female Dupont connector in **Figure 3**. This picture was taken after removing the black encasing on the red wire. The yellow arrows show you where the crimp was made to the red wire. 

For prototyping purposes, it is sufficient to just use jumper wires to connect components to the Arduino or to the breadboard. For permanent wiring, the component lead can be inserted directly into the bare-bone female Dupont pins that have their encasing removed, and then the two parts can be soldered together **(Figure 5).** 

<p align="center">
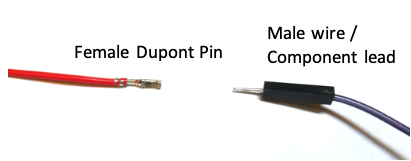
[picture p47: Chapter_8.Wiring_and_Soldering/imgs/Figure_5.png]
    <br><br>
    <b><i>Figure 5:</b> Sliding in the male pin to the female Dupont connector with the encasing removed </i>
</p>

<p align="center">
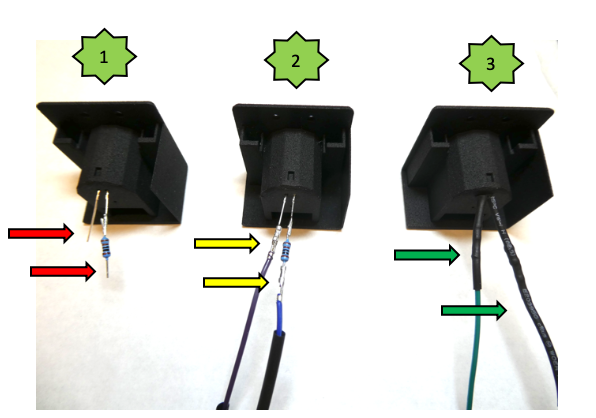
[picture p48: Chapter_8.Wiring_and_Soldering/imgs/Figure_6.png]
    <br><br>
    <b><i>Figure 6:</b> LED wiring stages </i>
</p>

The above picture **(Figure 6)** depicts the wiring schemes in different stages. In stage 1, the component leads are shown. In stage 2, the jumper wires have the black encasings removed. (yellow arrows) Also in stage 2, the male pins were connected to the female Dupont pins. To make them permanent, I have made a solder connection where the male pin and the female Dupont pin overlap. And finally in step 3, the heat shrink is heated with a lighter. Note that the appropriately sized heat shrink tubes before you make the solder connection between the wires and the component.

<p align="center">
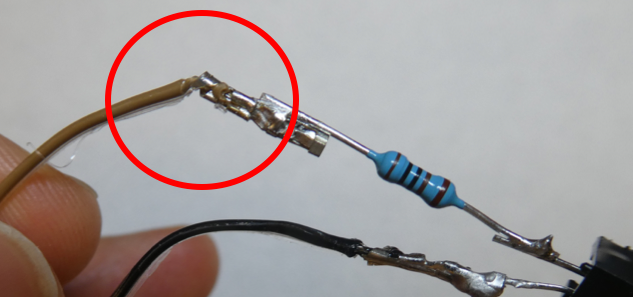
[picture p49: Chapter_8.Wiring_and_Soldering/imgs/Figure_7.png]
    <br><br>
    <b><i>Figure 7:</b> Fraying of the wire at the crimp junction (red circle). Excess solder probably weakened the crimp connection. </i>
</p>

### Example: Photo interrupters

The same method is used to solder the IR photo interrupters to the jumper wires (female – to – male 30 cm long). 

<p align="center">
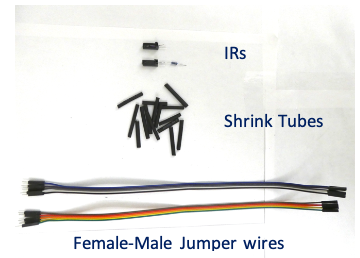
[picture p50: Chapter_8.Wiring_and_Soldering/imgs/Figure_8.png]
    <br><br>
    <b><i>Figure 8:</b> Materials Needed for IR - wire soldering </i>
</p>

<p align="center">
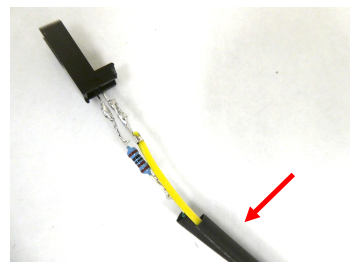
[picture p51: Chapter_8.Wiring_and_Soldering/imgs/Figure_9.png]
    <br><br>
    <b><i>Figure 9:</b> Wiring the IRs. Notice the heat shrink tubes (red arrow) </i>
</p>

<p align="center">
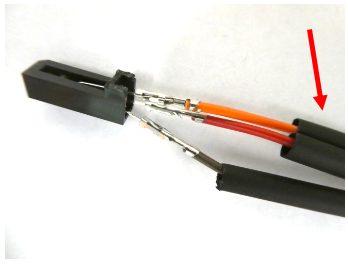
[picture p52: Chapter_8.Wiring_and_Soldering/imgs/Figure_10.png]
    <br><br>
    <b><i>Figure 10:</b> Wiring the phototransistors. Notice the heat shrink tubes (red arrow) </i>
</p>

<p align="center">
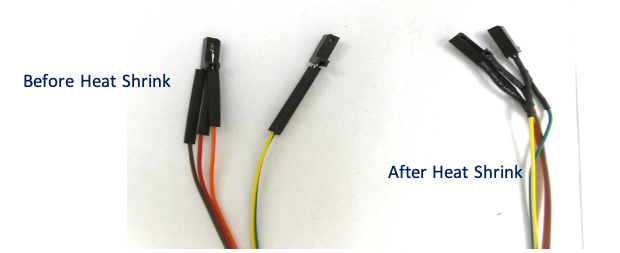
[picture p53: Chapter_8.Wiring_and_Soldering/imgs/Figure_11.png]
    <br><br>
    <b><i>Figure 11:</b> Completed wiring. Before and after applying heat to shrink tubes. </i>
</p>

###### END OF CHAPTER

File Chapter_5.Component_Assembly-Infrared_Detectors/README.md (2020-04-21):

# Component Assembly - Infrared Photo Interrupters 

Basics of IR photo interrupters and how to test them.
____

### Introduction
Infrared (IR) photo interrupters are sensors that can detect behavioral responses (rodent nose poke breaking a beam).

***Note:***IR photointerrupters* and *IR detectors* are used interchangeably here.

### What are IR detectors?

IR detectors are composed of: IR LED and a photo transistor. The basic working principle is that light and electricity signals are constantly getting converted through a certain medium. Once powered on, the IR LED of the photo interrupter will emit infrared light. The photo transistor, which is located across from the IR LED, will catch that light and convert it back to an electrical signal.

<p align="center">
    <br><br>
    <b><i>Figure 1:</b> LEDs convert current to light and photo transistors convert light to current. Image Source: <a href="https://www.rohm.com/electronics-basics/photointerrupters/what-is-a-photointerrupter"> Link </a></i>
</p>

Therefore, if the photo transistor can receive light from the IR LED (absence of object in light path), it will convert light signals to HIGH electric signals. In contrast, if a photo transistor cannot receive light (presence of object in light path), then the photo transistor can’t convert any incoming signals so the electric signal would result in LOW.

<p align="center">
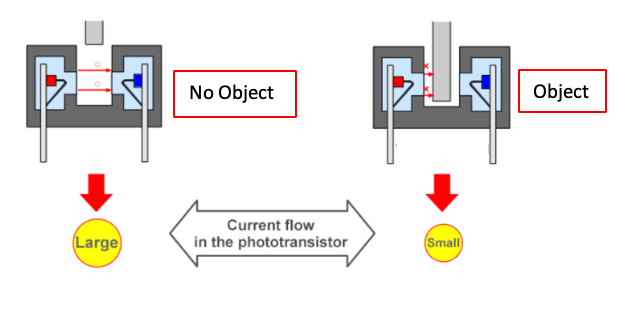
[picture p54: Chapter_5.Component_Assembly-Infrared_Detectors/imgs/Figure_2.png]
    <br><br>
    <b><i>Figure 2:</b> Basic diagram of how light and electric signals get converted. Image Source: <a href="https://www.rohm.com/electronics-basics/photointerrupters/what-is-a-photointerrupter"> Link </a></i>
</p>

This is how photo interrupters detect state changes in motion. For example, if a mouse nose pokes and “breaks” the light path of the IR LED, photo transistors won’t be able to receive that light and will accordingly output LOW electric signal, notifying us that some activity is present.

### Photo Interrupter GP1A57HRJ00F

We use this photo interrupter [GP1A57HRJ00F](https://www.sparkfun.com/products/9299), but there are many similar options.  

<p align="center">
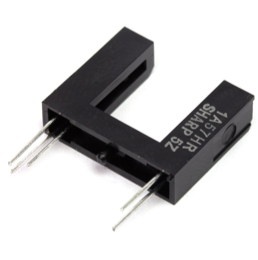
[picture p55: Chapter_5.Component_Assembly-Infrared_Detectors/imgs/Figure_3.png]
    <br><br>
    <b><i>Figure 3:</b> IR photo interrupter GP1A57HRJ00F </i>
</p>

Once you have the component, it needs to be powered and connected to the Arduino! To do that, consult the [datasheet](https://www.sparkfun.com/datasheets/Components/GP1A57HRJ00F.pdf) for this particular photo interrupter so it doesn't short the circuit prematurely. Below is an internal connection diagram from the official datasheet, and a “translated” version of the diagram (diagram 4). Note that diagram 3 and diagram 4 are top-down views of the photo interrupter. Also note that in diagram 4, the placement of the resistor doesn’t matter – it could as well be connected to ground and it will work just fine (as long as it’s a serial connection).

<p align="center">
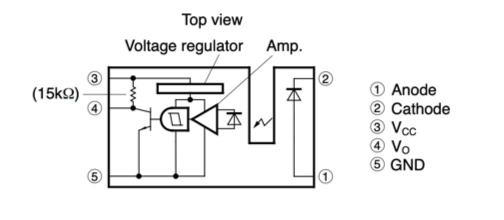
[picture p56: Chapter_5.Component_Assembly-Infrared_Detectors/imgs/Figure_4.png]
    <br><br>
    <b><i>Figure 4:</b> Internal connection diagram for the photo interrupter GP1A57HRJ00F. Note how the Infrared LED and the phototransistor are not connected electrically. Diagram Source: <a href="https://www.sparkfun.com/datasheets/Components/GP1A57HRJ00F.pdf"> Official Datasheet </a></i>
</p>

<p align="center">
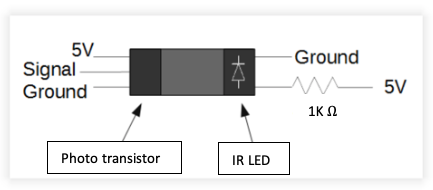
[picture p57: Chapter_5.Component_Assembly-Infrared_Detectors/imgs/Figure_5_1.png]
    <br><br>
    <b><i>Figure 5:</b> An easier “translated” version of the internal connection diagram in <b>Figure 4</b>. Image modified from: <a href="http://hmcbee.blogspot.com/2014/08/photogate-tutorial-part-2-basic.html?q=photogate"> Harvey Mudd Bee Lab </a></i>
</p>

### Breaking off the IR photo interrupter

The IR LED and the photo transistor are not connected electrically, so breaking it in half is possible as long as the light path of the IR LED to the photo transistor are aligned. This will effectively change the working distance between the two components.

<p align="center">
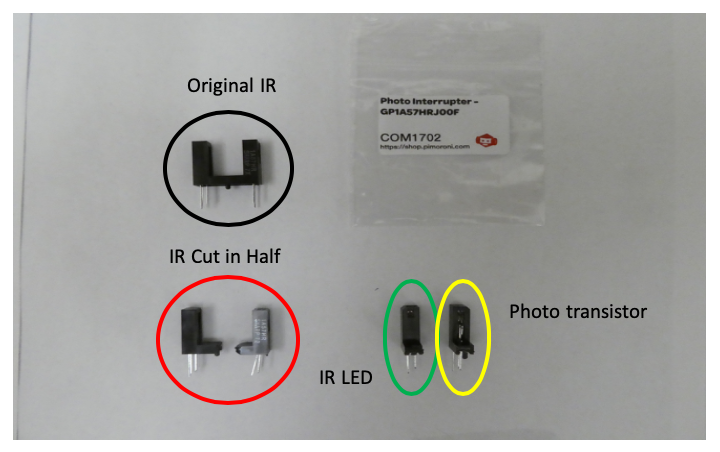
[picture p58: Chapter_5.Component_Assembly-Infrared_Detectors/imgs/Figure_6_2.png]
    <br><br>
    <b><i>Figure 6:</b> IR photo interrupter broken into IR LED <b>(green)</b> and photo transistor <b>(yellow).</b>  </i>
</p>

IR LEDs are LEDs which also need current-limiting resistors. Interestingly for GP1A57HRJ00F IR LED, the shorter lead happens to be the anode (opposite from regular LEDs). Note again that you may connect the resistor to the cathode as well and the current will still be limited. The important part is connecting the anode to PWR and cathode to GND when you are actually wiring the photo interrupters to the Arduino.

### Testing the IR LEDs

Human eyes have a limited wavelength detection spectrum. We can only detect wavelengths of light that are approximately 400 $nm$ – 700 $nm$. Therefore, it is not possible to “see” infrared light with the naked eye and to “see” if the IR LEDs are working or not.

<p align="center">
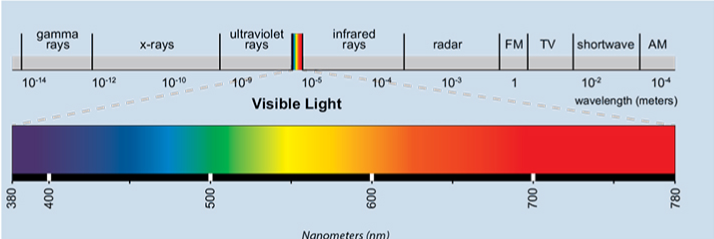
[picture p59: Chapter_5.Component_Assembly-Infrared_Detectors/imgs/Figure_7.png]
    <br><br>
    <b><i>Figure 7:</b> Light spectrum. Infrared rays have longer wavelengths (700 $nm$ ~ 1 $mm$) than visible light.</i>
</p>

Luckily camera lenses are more sensitive to light than our eyes are. They can actually “see” (detect) infrared light. This allows us to “see” the infrared light through our camera lens. Test it out yourselves. Take only the IR LED part from the photo interrupter, wire it correctly to the Arduino (anode to GND, cathode to PWR) and power the Arduino with the USB. Turn on your phone camera and shine it over the IR LED. You’ll be able to see a purple glow like in **Figure 8**. This is actually pretty useful and important to us because we want to test the IR LEDs for any defects just like we tested the regular LEDs. If you don't see the purple glow under your phone camera even after powering up the Arduino, that means the IR LED has gone out.

Going slightly off topic, you can use this trick to "see" how remote controls communicate with TVs. More info [here](https://www.businessinsider.com/phone-camera-trick-can-see-infrared-light-tv-remote-2015-9).

<p align="center">
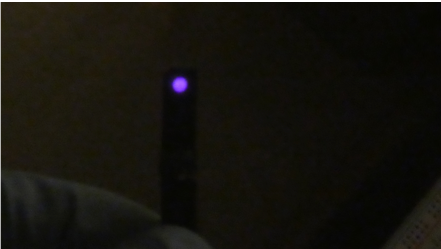
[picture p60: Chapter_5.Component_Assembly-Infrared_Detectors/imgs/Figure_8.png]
    <br><br>
    <b><i>Figure 8:</b> The purple glow of infrared light seen under a phone camera </i>
</p>

###### END OF CHAPTER

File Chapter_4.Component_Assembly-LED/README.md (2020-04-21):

# Chapter 4. Component Assembly - LEDs (Light Emitting Diodes) and Custom 3D printed noseports 

#### What you will learn:

Basics of LEDs and how to assemble them with the custom nose ports
___

### Introduction
LEDs (light emitting diodes) are incorporated into the customized nose ports to function as stimuli.

Noseport printing is outsourced to Shapeways. The design files are located <a href="https://github.com/DIY-NAMICsystem/Hardware_Documentation/tree/master/Shapeways_Final"> here. </a>

<p align="center">
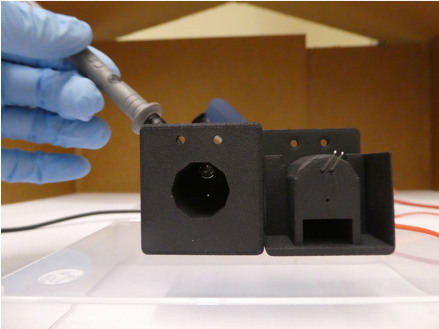
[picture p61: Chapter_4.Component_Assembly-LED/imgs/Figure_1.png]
    <br><br>
    <b><i>Figure 1:</b> The LED has been threaded through the holes in the noseports. <b>Left:</b> Front View / <b>Right:</b> Back View</i>
</p>

<p align="center">
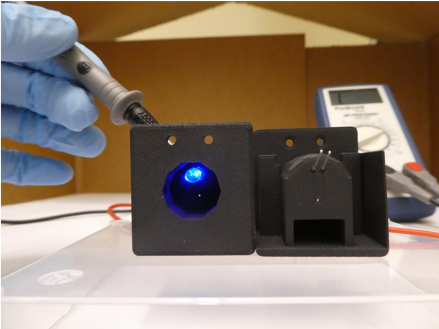
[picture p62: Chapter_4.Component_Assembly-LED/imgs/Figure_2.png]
    <br><br>
    <b><i>Figure 2:</b>  Using the multimeter to test the LED is helpful before soldering them in place. <b>Left:</b> Front View / <b>Right:</b> Back View</i>
</p>

### About LEDs

LEDs, or diodes in general, have two polarized legs. One is the cathode (-) and the other is the anode (+). In LEDs, the cathode tip (-) is shorter than the anode (+). What I mean by polarized is that there is a directionality in the current flow. LEDs won’t light up unless you connect the cathode to ground (GND) and anode to power (PWR). Circuit diagram in **Figure 4** shows this directionality clearly. In order to power up the LED, current must flow from the anode to the cathod. And just a quick refresher for the engineering students reading this manual. The little diagonal arrows going in the 1 o’clock direction in the circuit symbol signifies that it is a light-emitting diode. Without the small arrows, the circuit symbol would signify a diode.

<p align="center">
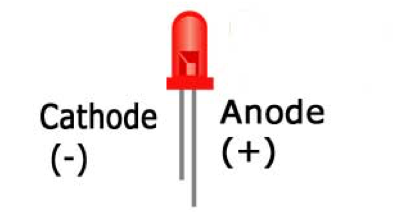
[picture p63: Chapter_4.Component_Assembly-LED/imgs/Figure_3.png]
    <br><br>
    <b><i>Figure 3:</b> LED with the cathode lead and the anode lead. Image Source: <a href="http://sciencewithkids.com/science-facts/facts-about-LEDs.html"> Link </a> </i>
</p>

<p align="center">
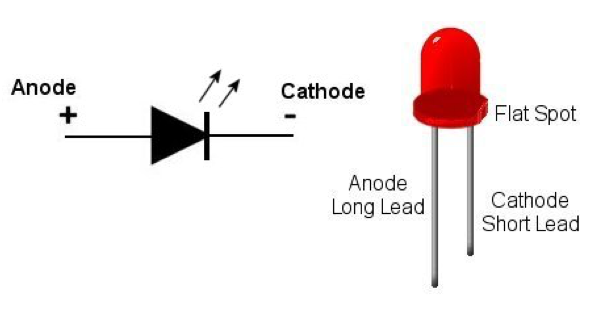
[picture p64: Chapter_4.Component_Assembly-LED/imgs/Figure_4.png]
    <br><br>
    <b><i>Figure 4:</b> Diagram of how current flows in an LED. Note how the <b>flat (blunt) spot</b> is the cathode tip. Image Source: <a href="http://www.mainbyte.com/ti99/electronics/led.html"> Link </a> </i>
</p>

### Importance of Current-Limiting Resistors

The brightness of an LED depends directly on how much current it draws. So the more current it draws, the brighter it is going to be. The forward current increases exponentially as a function of forward voltage. (If the terms forward current ($I_{f}$), forward voltage ($V_{f}$)are unfamiliar to you, it simply means how much current and voltage is being run across that component.) Too much current equals too much power and too much heat, which will eventually burnout the LED and could also potentially damage the whole circuit (including the Arduino). 

<p align="center">
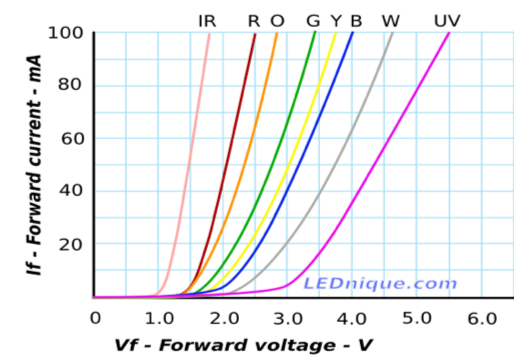
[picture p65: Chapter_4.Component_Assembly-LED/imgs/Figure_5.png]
    <br><br>
    <b><i>Figure 5:</b> IV curve (current versus voltage curve) for different types of LEDs. You can notice that the current increase is exponential as a function of forward voltage. Image Source: <a href="http://lednique.com/current-voltage-relationships/iv-curves/"> Link </a></i>
</p>

Essentially this is why we need current-limiting resistors for LEDs. The name is self-explanatory. Resistors prevent excessive current flow to LEDs so that they may operate under maximum forward current ($I_{f}$) and not burn themselves out. Typically, the maximum forward current is 20mA for most LEDs.

To calculate current-limiting resistor values for different types of LEDs, you can use this [resistor value calculator](https://www.digikey.com/en/resources/conversion-calculators/conversion-calculator-led-series-resistor), but if you just want the short answer/want to play it safe, we use 1k Ω for our blue LEDs. Considering that blue LEDs typically have a forward voltage of 3.0V, this will effectively give us 2mA of operating current for the LED. For more information on picking resistors for LEDs, check out [this blog](https://www.evilmadscientist.com/2012/resistors-for-leds/) from **evilmadscientist.com**

### Soldering LEDs

#### Note of Warning

>Do a simple continuity test with a multimeter on the LEDs so that you know that the LEDs are not faulty. Remember to connect the anode to PWR (red) and cathode to GND (black). Additionally, if you have a breadboard and an Arduino in hand, you can just hook up a simple circuit with a resistor to test out that the LEDs are working.

Since everything will be connected in series, the current limiting resistor can go on either anode or cathode. The LEDs will receive a dialed-down current no matter where you connect the resistor. To standardize things however, we will solder the resistor to the cathode (-) so that it will be easier to distinguish the cathode terminal. As I’ve mentioned before, the cathodes have shorter leads than anodes. If you’ve already cut the terminals however, and can’t distinguish the length, there are other ways to tell. If you look at **Figure 4**, you will see that the cathode tip has a flat surface on the LED. On the other hand, anodes will have a rounder surface. Since cathodes connect to GND, I like to remember this scheme as **“blunt is black”** (Electrical engineers typically color code PWR with red and GND with black).

###### END OF CHAPTER

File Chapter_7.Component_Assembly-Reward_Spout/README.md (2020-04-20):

# Chapter 7. Component Assembly - Reward Spout

#### What you will learn:

Cutting the hypodermic needles with a Dremel and fitting them with Luer Lock adapters and appropriate tubing to make the reward spout.
____

### Introduction

Solenoids (from the Lee Company) are used to dispense liquid in the DIY-NAMIC system. 

### Step-by-step Tutorial

1. Get a 21G Needle (0.8 mm x 50 mm) – Different gauge needles will output volumes at different rates. (Use a trial and error process to determine the solenoid on duration for a target output volume. With our components and a 21G needle, turning on the solenoid for 72 ms results in 10 ul of volume (water) output.

<p align="center">
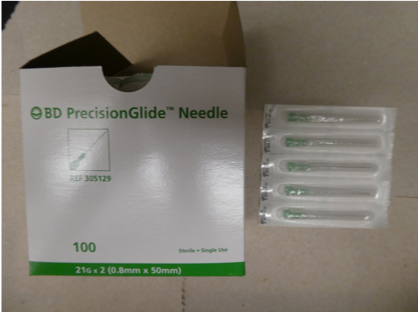
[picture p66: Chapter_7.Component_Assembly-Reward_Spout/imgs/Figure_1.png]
    <br><br>
    <b><i>Figure 1:</b> Get 21G hypodermic needles </i>
</p>

2. Mark off 1.5cm from the base of the needle (orange line). Always measure a little bit more than 1.5cm with a thick sharpie since manually operated Dremel will be imprecise.

<p align="center">
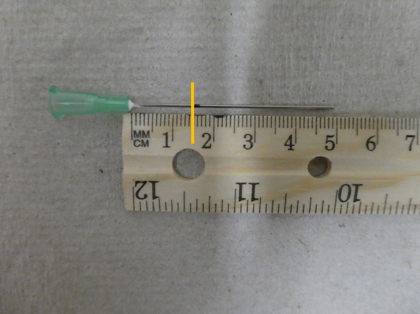
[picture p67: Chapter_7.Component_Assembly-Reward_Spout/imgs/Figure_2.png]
    <br><br>
    <b><i>Figure 2:</b> Mark off 1.5 cm from the base of the needle </i>
</p>

3. With a Dremel fitted with an EZ Lock ***metal*** cutting wheel, cut the hypodermic needle at the Sharpie marking

4. After you make the cut, sand down the needle tip with a belt grinder (or manual metal filer). Ensure end is open and smooth.

<p align="center">
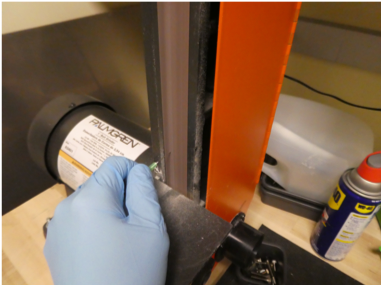
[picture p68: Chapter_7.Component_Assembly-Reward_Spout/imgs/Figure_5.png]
    <br><br>
    <b><i>Figure 5:</b> Using the belt grinder to sand down the needle spout. </i>
</p>

<p align="center">
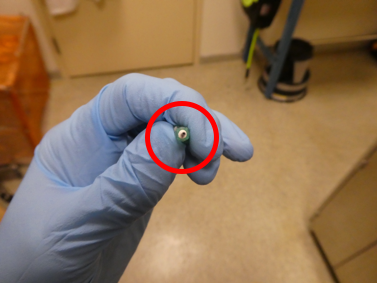
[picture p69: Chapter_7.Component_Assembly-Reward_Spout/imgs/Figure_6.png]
    <br><br>
    <b><i>Figure 6:</b> It is a bit hard to see, but the tip of the needle is sanded down. <b>(Red Circle)</b> </i>
</p>

5. Assemble the needle with Luer Lock adapter and tubing (Part #: TET-062A - See [Bill of Materials](https://github.com/jhl0204/AIM-Hardware-Documentations/wiki/Bill-of-Materials)). The length of tubing for the solenoid needle should be around 9 cm to minimize the kinking. The other end of the tubing should be fitted to the middle port of the solenoid valve. **(Figure 8)**

<p align="center">
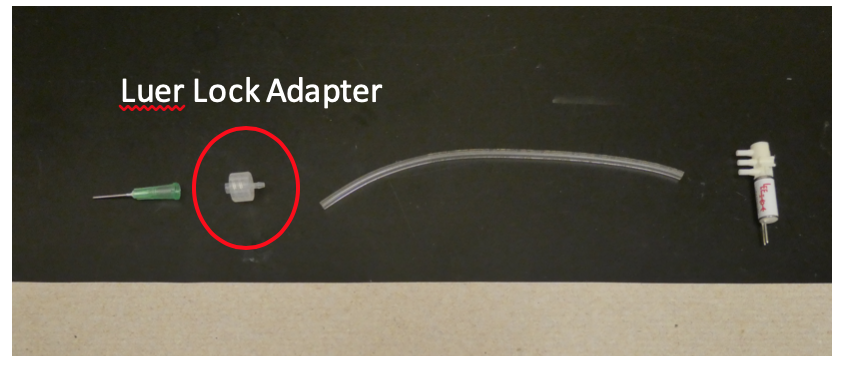
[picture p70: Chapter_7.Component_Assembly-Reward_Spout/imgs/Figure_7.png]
    <br><br>
    <b><i>Figure 7:</b> From Left to Right: Needle, Luer Lock adapter, Tygon E-3603 Tubing (Part #: TET-062A), Solenoid Valve </i>
</p>

<p align="center">
    <br><br>
    <b><i>Figure 8:</b> The other end of the tubing should fit onto the middle port of the solenoid valve. <b>(Red Circle)</b> </i>
</p>

###### END OF CHAPTER

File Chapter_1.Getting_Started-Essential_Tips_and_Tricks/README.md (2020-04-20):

# Chapter 1. Essential Tips and Tricks

____  
### Introduction
This page covers some basic knowledge and skills for those less familiar with building electronic platforms. 

### 1. Multimeter

Multimeters are a useful debugging tool for this project. [Amazon Link to Multimeter](https://www.amazon.com/AstroAI-Digital-Multimeter-Voltage-Tester/dp/B01ISAMUA6/ref=sr_1_1_sspa?keywords=multimeter&qid=1571619926&sr=8-1-spons&psc=1&spLa=ZW5jcnlwdGVkUXVhbGlmaWVyPUFINUcyVlJPTUk2S0gmZW5jcnlwdGVkSWQ9QTA4NTQ4Mzg1U0pNUlYxREUzN0QmZW5jcnlwdGVkQWRJZD1BMDAzNzc5MTNNMU05T1dXRVhWMEQmd2lkZ2V0TmFtZT1zcF9hdGYmYWN0aW9uPWNsaWNrUmVkaXJlY3QmZG9Ob3RMb2dDbGljaz10cnVl)

Multimeters can measure a lot of things including continuity, resistance, voltage, current, capacitance etc. But the most useful functionality (in my opinion) is the continuity / diode testing mode. This functionality allows you to check if a diode is working or not (which has directionality), and whether two points in a circuit are electrically connected or not. The multimeter will beep (output of a piezo buzzer) if the two points are connected and will light up the LED if the cathode is connected to GND and anode is connected to PWR. But always remember to turn the knob to continuity / diode testing mode before testing anything! Otherwise the multimeter would be powered off.

<p align="center">
    multimeter<br><br>
    <b><i>Figure 1:</b> Continuity test mode shown on the multimeter (white circle). The value on the display indicate the resistance value. Value “1” signifies that it’s an open loop. </i>
</p>

<p align="center">
    continuity_symbol<br><br>
    <b><i>Figure 2:</b> Close up view of the continuity / diode testing option </i>
</p>

To provide more perspective, continuity testing is extremely useful in verifying your solder joints either on the printed circuit boards (PCB) or on any other wires. If you’ve soldered something on, probed the two solder points and got a beep, that means the two points are connected. Now this might be good or bad depending on each case. If you meant to connect the two points, then you're all set. If the two points are **NOT** supposed to be connected, then you have a short circuit. This means you’ll have to redo the solder connection, but doing this now will save you a ton of time in the future when you’re running your software on the circuit board and the hardware component is not working as you expected. (Hardware will not work properly if there is a short circuit!).

Below is a summary I found on [Adafruit.com](https://learn.adafruit.com/multimeters/continuity) on various things the continuity test can be useful for:

<p align="center">
continuity_testing
</p>   

#### Using the multimeter for this project

To make DIY-NAMIC boxes, the following major components are needed: PCB / LEDs / IRs/ and solenoids.

Using the multimeter on the PCB is fairly straightforward. If you want to verify connections between two points, you can probe it using the clips. If It’s connected, you should hear a beep. Using the multimeter on LEDs is simple as well. Once you connect them correctly, ***(cathode to GND / anode to PWR)*** the LED will light up (you will not hear any beeps). For IR LEDs, you won’t “see” the IRs light up because human eyes can’t detect infrared light but ***there are [tricks](https://nbviewer.ipython.org/github/jhl0204/DNAMIC-Hardware-Documentations/blob/master/Chapter_5.Component_Assembly-Infrared_Detectors/5_Component_Assembly_IR_vF.ipynb) you can use to "see" the IRs***. For solenoids, it’s a little different story. If you test out the two leads, although the two leads are not touching each other, the multimeter will give you a beep. 

<p align="center">
  solenoid<br><br>
  <b><i>Figure 3:</b> Red arrow indicates Power (PWR) and the black arrow indicates Ground (GND) </i>
</p>   
See here for more info: [solenoid valve section](https://nbviewer.ipython.org/github/jhl0204/DNAMIC-Hardware-Documentations/blob/master/Chapter_6.Component_Assembly-Solenoid_Valves/6_Component_Assembly_Solenoid_Valves_vF.ipynb). The solenoids are actually continuous cylindrical coil of wire. The two leads you see in **Figure 3** are two ends of the same wire. The cylindrical coil is hidden inside the component. The exact resistance of the coil will depend on a lot of things, but it will tend to be very low and seem like a short circuit. If they don't have a low resistance, then it's likely that the wire has broken internally, and the valve is dead. So to sum it up, the “beep” you hear when you test out the continuity on the solenoid valves means that the valves are working!

### 2. Breaking off Pins

Breaking off header pins (especially female types) correctly is surprisingly difficult. If you try breaking them off with a wire cutter, you’ll notice that often times you end up with one less header than you intended because the encasings break off. Thus, this method of using the wire cutters is very unreliable when you want to get a specific length of the header pins.

<p align="center">
  <br><br>
  <b><i> Figure 4:</b> Two types of header pins – Female (red circle) and Male (green circle) pins. </i>
</p>

<p align="center">
  <br><br>
  <b><i> Figure 5:</b> An example of an improper way of breaking off pins. Notice that the metal header pin has fallen off from the black encasing.</i>
 </p>

--------------
 
 #### Making a 1x4 header pin

1. As a first step, you need to remove the $(n+1)^{th}$ pin from the parent bulk of pins. You can see from the yellow arrow in **Figure 6** that the 5th pin has been removed since our goal is to get a 1 x 4 pin.

<p align="center">
  <br><br>
  <b><i> Figure 6:</b> Female header pins after removing the (n+1)th pin. This location will later serve as the spot to make etched guidelines.</i>
 </p>

2. Next, you want to make **“cutting guidelines”** into the 5th encasing. The encasings are made of plastic so it’s pretty easy to do. You can see the etched guidelines in the red circle in **Figure 8**. Make these guidelines on both sides of the encasing. After making the guidelines, you can just snap them off. The header will easily snap off along the guidelines you have created.

<p align="center">
  <br><br>
  <b><i> Figure 7:</b> Making the cutting guidelines with a wire cutter </i>
 </p>

 <p align="center">
   <br><br>
   <b><i> Figure 8:</b> It might be a little hard to see, but you can fainlty notice the etched guidelines at the empty pin location (red circle) Once you have the guidelines, gently snap them off along the guidelines to get the finished product. </i>
  </p>

  <p align="center">
    <br><br>
    <b><i> Figure 9:</b> We have successfully made a 1x4 female header pin! Compare and contrast this to **Figure 5** where we failed to properly break off the pin size of our interest. </i>
   </p>

3. As a final touch, you can sand down these headers using a belt grinder (or with normal sandpaper) to give them a cleaner, smoother finish. The smooth finish will not only give the finished product a more professional look but also allow other components to fit better on the board.

<p align="center">
  <br><br>
  <b><i> Figure 10:</b> Before <b> red rectangle </b> and after <b> green rectangle </b> sanding down the headers. Notice the smoother finish in the 'after' products </i>
 </p>

 ### 3. Soldering Components to PCB

When soldering anything onto a PCB, you want the components to be flush with the board. Simply put, you don’t want your components to look like the X-marked headers in **Figure 1** below. This is surprisingly pretty tricky to do because headers tend to move around a lot when soldering. As you go through the pins in a serial fashion, you’ll quickly realize one small misalignment will lead to the misalignment of the whole component (like in **Figure 1** below) because solder joints cool down and harden very quickly.

<p align="center">
  <br><br>
  <i> Examples of good soldered (first and third) and bad soldered headers (second and fourth) <i/>
 </p>

 #### Soldering Components Flush with the board

The basic idea behind this trick is to temporarily affix the components / headers flush with the board with some tape, and soldering key anchor points to the board. Once you have the anchor points, you can take the tape off and solder the remaining leads to the board. I’ll use the stacking pins as an example to demonstrate this method.

1. Use tape to fixate the components / headers to the shield so that it doesn’t fall off even when the board is upside down

<p align="center">
  <br><br>
  <b><i> Figure 11:</b> Use tape to affix the stacking pins to the shield. (Top-down view) </i>
 </p>

 2. With the tape attached, solder just the two ends of the stacking pins so that you can take the tape off. These will be your anchor points.

 <p align="center">
   <br><br>
   <b><i> Figure 12:</b> Stacking pins after the anchor points (white circles) have been soldered on. Notice the silver solder joints within the white circles </i>
  </p>

3. Note that step 2 will not anchor the stacking pins perfectly flush with the shield (red box in **Figure 14**). To anchor the stacking pins flush with the shield, heat up your anchor solder joints and push in / wiggle the stacking pins against the shield until you feel that the stacking pins are flush.  

<p align="center">
  <br><br>
  <b><i> Figure 13:</b> Note that the stacking pins are not yet flush with the shield (red box). </i>
 </p>

 4. After adjusting the stacking pins and your anchor points, it’s time to solder in the remaining holes. If you feel that the stacking pins are getting misaligned as you solder, repeat step 3 so that the stacking pins are actually flush with board.

 <p align="center">
   <br><br>
   <b><i> Figure 14:</b> Bottom view of a finished solder work. Note all the solder connections (red box). </i>
  </p>

  <p align="center">
    <br><br>
    <b><i> Figure 15:</b> Side view of a finished solder work. Notice that the stacking pins are flush with the shield. Compare this image with <b> Figure 11 <b/>.</i>
   </p>

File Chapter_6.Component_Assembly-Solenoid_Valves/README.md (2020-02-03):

# Chapter 6. Component Assembly - Solenoid Valves

#### What you will learn:

Basics of solenoid valve operation, testing, and assembly + manifolds
___

### Introduction - What are solenoid valves?

A solenoid valve is an electromechanical device in which the solenoid uses an electric current to generate a magnetic field and thereby regulate fluid flow using a valve. Simply put, the magnetic field created by solenoids are what switches the valves on and off. Then what are solenoids? **A solenoid is a cylindrical coil of wire acting as a magnet when carrying electric current.** Solenoids are actually easily confused with electromagnets, but the key difference is that the solenoids don’t have a metal core in the center. If there was a magnetic core, then it would be an electromagnet and the strength of the magnetic field would be proportional to the electric current. Without the magnetic core, the wires would be called a solenoid and exist only in binary on and off states. This is why solenoids are used as simple binary switches in electrical systems.

<p align="center">
    <br><br>
    <b><i>Figure 1:</b>Example of a solenoid. Note the absence of a magnetic core. Note that these solenoids are inside the solenoid valves. </i>
</p>

<p align="center">
    <br><br>
    <b><i>Figure 2:</b> Different types of solenoid valves. </i>
</p>

For the DNAMIC boxes, we use the solenoid valves to control the flow of reward. There are a lot of different types of solenoid valves out there and you should explore the different types that best fit your own needs. In our lab, we use [LHDA0531115H](https://www.theleeco.com/products/electro-fluidic-systems/solenoid-valves/control-valves/lhd-series/3-port/ported/) (3-port ported solenoid valves) because they are compact, and we are able to attach appropriate tubing to effectively lengthen the distance of reward delivery.

____

### Solenoid Valve LHDA0531115H

The following is the solenoid valve we use in the lab. As you can notice from **Figures 3 and 4**, it is very small and has 3 ports.

<p align="center">
    <br><br>
    <b><i>Figure 3:</b> Use starburst for comparison! </i>
</p>

<p align="center">
    <br><br>
    <b><i>Figure 4:</b> Notice that the top port is closed off and the bottom two ports are open. </i>
</p>

You might also notice from **Figure 4** that the top port is closed off and the bottom two are open. I won’t go into the details of how solenoid valves work, but basically the solenoids control the opening and closing of the ports by releasing or obstructing the openings of the ports using a plunger (**Figure 5**). And with electrical current, we can control how long the valves stay open or closed. That’s how solenoid valves can dispense water (or any liquid or gas). Let's also look at a diagram from the official specification sheet to understand the solenoid valves better.

<p align="center">
    <br><br>
    <b><i>Figure 5:</b> Cross section view of the solenoid valve. Solenoid coil (green) controls the plunger (blue) which in turn determines which of the three ports will be open. </i>
</p>

<p align="center">
    <br><br>
    <b><i>Figure 6:</b> Diagram of the ports in solenoid LHDA0531115H. Note that the ports are either <b>‘normally closed’, ‘common’, or ‘normally open’</b> / Source: Lee Company </i>
</p>

As you can see from **Figure 6** the top port is 'normally closed' while the bottom port is 'normally open'. The middle port is 'common'. To be perfectly honest, I am not sure what this means or why the solenoids are designed like so. ***(Comments / Pull Requests / Feedback would be much appreciated from the enginnering community out there!)*** From what I've figured out however, I can control the fluid flow using the middle and top ports when the solenoid valve is powered up. Also, since the bottom port is “normally open”, we need to cap the port so that the fluid doesn’t leak during operation. In order to make the cap, I’ve just burned one side of the tubing and fitted it over the bottom port. **(Figure 7)**

<p align="center">
    <br><br>
    <b><i>Figure 7:</b> Tubing have been burnt at one end to be used as caps for the bottom port of the solenoid valve. </i>
</p>

### Manifolds

DNAMIC boxes were designed to hold three noseports and thus three reward centers. Each reward center requires a solenoid valve which in turn requires a separate reward (fluid) source. However having a reward source for each solenoid valve is spatially expensive. Could there be a hardware that can solve this problem? Meet manifolds. Manifolds are chambers that branch into several openings, just like in **Figure 8** where the manifold branches out into 3 different ports or outlets (see the numberings 1, 2 and 3 in the figure). Our lab picked this [particular manifold](https://www.mcmaster.com/catalog%2f125%2f237) (Ref #: 5203K929) because it would allow fluid control to 3 different solenoid valves using just one syringe as an inlet source. These are also push-to-connect manifolds meaning that you can just push in the appropriate tubing into the orange outlet and the “claws” within the port will clamp down on the tubing and hold it down. Just make sure that the tubing end is cut evenly since a slanted cut will affect the effectiveness of the clamp. When inserting the tubing, make sure to pull out the orange O-ring completely, insert tubing, and push in the orange O-rings again. The tubing specifications used for the solenoid valves and manifolds can be found in the [Bill of Materials](https://github.com/jhl0204/AIM-Hardware-Documentations/wiki/Bill-of-Materials) (Part #: TET-062A)

<p align="center">
    <br><br>
    <b><i>Figure 8:</b> Diagram of how the fluid will flow in the system. White arrows denote the direction of fluid flow. The dashed arrows signify that it will flow only when solenoid valve is powered up. Note that only one solenoid valve was shown in this example. Also note that the tubing from manifold is attached to the top port of the solenoid valve and the tubing from reward spout is attached to the middle port. </i>
</p>

<p align="center">
    <br><br>
    <b><i>Figure 9:</b> Push-to-connect manifolds side by side. The orange O-ring is where the tubing goes in and can slide in and out. </i>
</p>

The tubing that goes into the manifold will connect to the top port of the solenoid (refer to **Figures 4 and 6**). When the manifold is fitted onto the manifold encasing, the length required for the tubing to reach the solenoid is about ~13cm. However, you can’t extend the length of the tubing after a cut, so give yourself some extra length and cut about 15cm for the tubing. These push-to-connect manifolds are prone to leaks and you might end up readjusting (pull out and re-insert) often.

<p align="center">
    <br><br>
    <b><i>Figure 10:</b> Manifold fitted with appropriate tubing. The numbers represent the number of outlets. </i>
</p>

The manifolds are also more prone to leakage when placed vertically. They will be lying horizontally on the encasings in the finished product however, so as long as the manifolds don’t leak when laid horizontally, you don’t need to worry about the leak. If they keep leaking after multiple adjustments however, try to identify the source and glue it in with Loctite 401. Personally, I found that the juncture between the body and the orange O-ring turns out to be the source of the leak 90% of the time, so that’s where I would use Loctite **(Figure 11)**. Going forward however, I believe a new manifold is needed since more than 80% of the outlets have been leaking with the normal push-to-connect mechanism.

<p align="center">
    <br><br>
    <b><i>Figure 11:</b> Red arrow represents where I have glued the orange slider to the body. Green arrows indicate that no glue was used. </i>
</p>

###### END OF CHAPTER

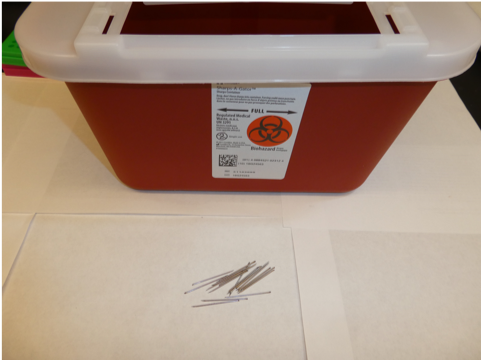
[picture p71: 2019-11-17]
Chapter_7.Component_Assembly-Reward_Spout/imgs/Figure_3.png

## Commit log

2019-11-18 added bill of materials
    [AIM_Bill_of_Materials.xlsx]
2020-02-20 Upload shapeways and ponoko files
    3 Shapeway stl files & 1 Ponoko eps file!
    [Individual_Ports.stl, manifold_encasing_bottom.stl, manifold_encasing_top.stl]
